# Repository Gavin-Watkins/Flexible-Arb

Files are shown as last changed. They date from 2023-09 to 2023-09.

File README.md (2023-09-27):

# Flexible Arduino Due based Arbitrary Signal Generator
Often during a project I have needed a complex test signal that is beyond the capability of the signal or function generators available in my lab. Commercial arbitrary signal generators (ARB) consisting of a fast memory coupled to a digital-to-analogue converter (DAC) are available, but often do not offer the right mix of analog and digital outputs in a suitably flexible (and affordable!) form. This has also been a problem during my day job where I have need to drive a high efficiency radio frequency (RF) power amplifiers (PA) or transmitters with two analogue outputs for the in-phase (I) and quadrature (Q) inputs of an RF modulator and several digital outputs for switching parts of the transmitter. [Previous work used an ARB platform developed around an Arduino Mega2560](https://www.researchgate.net/publication/361063526_A_Digital_Power_Amplifier_for_32-QAM). This was limited to a sample rate of 457kS/s. To increase the sample rate a new ARB has been developed based on an Arduino Due offering up to 8.4MS/s.

The Arduino Due is based on the 32-bit ATSAM3X8E allowing multiple 8-bit DACs and digital outputs to be mapped onto a single port. This ensuring all DAC or digital outputs update at the same time and only a single LUT is call for every update. The Arduino Due also runs at a higher clock rate of 84 MHz. Although 32-bit, none of the four ports (A to D) available on the ATSAM3X8E’s pins map to all 32-bits. Of the four ports, C with 24-bits available is the most useful. These 24 bits in this project are connected to two 8-bit DACs and one 8-bit digital port. However, they could for example drive two 12-bit DACs or any such combination.

# Testing the Arduino Due
The first thing anyone looks at with an ARB is the sampling rate. In a software based ARB like this (as oppose to an FPGA implementation) the microprocessor much fetch the output samples from memory and present them to the port with the DAC. This takes ten instruction cycles resulting in 8.4 MS/s as shown below in the minimum viable code:

start:                                // start of loop  

count = count + 1;                    // increment counter, takes two instruction

count = count & 0x000000FF;           // mask to prevent overflow from end of LUT, takes one instruction

PIOC->PIO_ODSR = Portvalues[count];   // access the LUT and send it to PortC, takes two instructions

goto start;                           // and repeat, takes five instructions

The felixbility of this option opens up other possiblities, like adding a second port which reads from its own LUT. PortA offers 23 bits, which would give a total of 47bits of data. This would however slow down the sample rate to 5.25 MS/s and require external latches for synchronising the data. This ran fastest when in Setup. Putting it in Loop resulted in slowing down. Why this is so, I'm not sure, but it is something I intend to explore further.

# DACs
The most important part of any ARB are the DACs. For this I settle on the DAC0801. Although quite old, they are readily available and easy to interface. Their datasheet quotes a settling time of 100ns consisting of the DAC slewing time and that for any ringing at the output to settle. The slewing time is a factor of the DAC output current and its load impedance. This suggests a maximum sample rate of 10 MS/s, which fits well with the 8.4 MS/s of the Due. The DAC0801 has complementary current sink outputs (pins 2 and 4). The datasheet suggests op-amp active current to voltage (I/V) converters as an output stage. This was found to introduce excess ringing, so passive resistive I/V converters were used instead. With a 1kΩ resistive load (RL) the slew rate was 30V/μs equivalent to a rise and fall time of 42ns. 

The DAC (IC1 and IC3) and op-amp (IC2 and IC4) interface is shown in the Eagle schematic "Sch6.sch" and as a png "Sch6.png". The peak output current of the DAC0801 is set at 2.13mA by the 4k7 resistors on pins 14 and 15 (R10, R14, R19 and R20) when a ±10V power supply is used. A 1k1 resistor tied to 0V and two 4k7 resistors in series (9k4) to +10 V positive supply rail add an offset so the output voltage at pin 4 swings positive and negative around 0V. This is a high impedance port so an op-amp with a gain of 2V/V buffers the output to drive 2V peak-to-peak into a 50Ω load. In the prototype a TL071 proved optimal in terms of bandwidth and ringing. Note in the schematic this is listed as a 741, simply because it was the first op-amp listed. The TL071 has a unity gain bandwidth product of 3MHz, reduced to 1.5MHz with a gain of 2V/V. Other op-amps may provide a better combination of bandwidth, slew rate and output current.

# Code
The Arduino Due can be programmed in the usual Arduino IDE, but has a unique set of instructions which allows direct port access. The following commands setup port C of the Due for direct access: PIOC→PIO_PER and PIOC→PIO_OER. The command PIOC→PIO_ODSR is then used to write data to the port. A goto loop sends data from the LUT to Port C runs in the setup, as using the main Void loop incurs various overheads including the I/O system to check the serial port. The result is 10 instructions and 8.4MS/s output rate. The LUT allocations are accessed by the variable count which is a 32-bit integer. This is masked (by ANDing) with FF (256) in the sinewave example, 1FF (512) in the triple test example and 4FFF (16384) for the 4G Long Term Evolution (LTE) signal example. Restricting the LUT to powers of 2 simplifies (and hence speeds up) the code. For other values an IF or FOR loop could be used to reset count at any value. A noInterrupts command to disable interrupts is included as without it jitter was noted on the output waveform suggesting the compiler sets some interrupts by default. If a lower sample frequency is desired though, the delayMicroseconds command can be included. In this case noInterrupts should be commented out.

# Data Generation
The data for all ports and the trigger signal are stored in a single LUT (Portvalues in the code). For Port C, the bits that are available on the external pins are: bits 1-8 for Ch A DAC, bits 12-19 for Ch B DAC, bits 21-26 for a digital interface and bit 28 as a trigger. These are generated individually and then mapped into a 32bit word which forms the values of Portvalues by multiplying the individual values by an offset and adding them together, for example:

Portvalues[X] = 2^28 x Trigger + 2^21 x Digital + 2^12 x DAC2 + 2 x DAC1

# Tool Chain 
The first two examples were generated in an OpenOffice spreadsheet (File "Signal Gen3.ods) as the LUTs were not very big. The third example was in Python ( due to the resulting LUT size. If using a spreadsheet the data will be generated in a single column. This can be copy and pasted directly into the Arduino IDE as a single column array. It is often more practical though to do this as a 2D array. The values from different cells can be combined with commas as a string into a single cell using the “&” function. In the sinewave example where the values of column Y are to be reformatted into a 16 column by 16 row for 256 values the following is used:

=Y2 & " , " & Y3 & ", " & Y4 & ", " & Y5 & ", " & Y6 & ", " & Y7 & ", " & Y8 & ", " & Y9 & ", " & Y10 & ", " & Y11 & ", " & Y12 & ", " & Y13 & ", " & Y14 & ", " & Y15 & ", " & Y16 & ", " & Y17 & ", "

Using the autofill function will not appropriately increment the Y column values, so there is still quite a bit of manual processing to be done, which is why for larger arrays it is appropriate to use Python. The Python code reads in the File "1M4LTE.txt". The sample rate of the LTE data is 7.68 MS/s, this is the original 122.88 MS/s downsampled by 16. Adding a dummy instruction to the Arduino code results in a sample rate of 7.64 MS/s. This is not close enough to 7.68 MS/s for standard compliance, but sufficient for measuring the adjacent channel power ratio (ACPR) of a PA/transmitter output.

# Hardware Implementation
To verify the concept, an Arduino Due “shield” was produced. This was fabricated on standard FR4 substrate using through hole DIL components. The layout is shown in "Sch6.brd" for Eagle and "Sch6_PCB.png" as a png. The Gerber files are in the zip file "Gerbers.zip". DIL components incur stray inductance and capacitance when operating in the MHz region, but allow the design to be easily modified. A surface mount implementation would probably produce better results than those presented here. 

The shield runs off a 5V supply for the digital and +/-10V for the analogue. The former can be extracted from the USB interface, as it is assumed that this project will be permanently connected to a computer for updating the LUT. The +/-10V can be derived from the 5V USB with a DC-DC converter and then smoothing and filtering.

# Example Results
The code includes three examples: a 32.8125kHz quadrature sinewave on DAC1 and DAC2 with a 256 value LUT (8.4MS/s / 256 = 32.8125 kHz), a triple tone test at around 1 MHz and the 4G LTE signal generation. Screen captures of these are shown to demonstrate the capabilities of the ARB. For the triple tone test the three tone frequencies are 984.375 kHz, 1.00078125 MHz and 1.0171875 MHz. These three resulting frequencies (Fr) were calculated with:

Fr = Fs * n / LUTs

Where Fs is the sampling frequency, n a whole number to avoid discontinuities – reducing spurious produces – and LUTs the LUT size. For an Fs was 8.4MS/s, n: 60, 61 and 62, and LUTs 512. Even with all the harmonically related spurious products, they are -38dB relative to the three tones. A higher resolution DAC would offer greater dynamic range, and hence lower spurious products. 

For the LTE signal, a screen capture of the spectrum of the I-channel signal is included. This includes guard channels, resulting in an actual RF bandwidth is 1.08MHz (consisting of six 180kHz resource blocks). The baseband bandwidth is half this, a spectrum of 504kHz as clearly shown in the example. The spectral regrowth is partially due to DAC non-linearities and also spurious products introduced by the system. uffers. The next phase of this research is to combine the LTE signal generator with a low-cost quadrature modulator development board to generate 4G signals for testing transmitter architectures.

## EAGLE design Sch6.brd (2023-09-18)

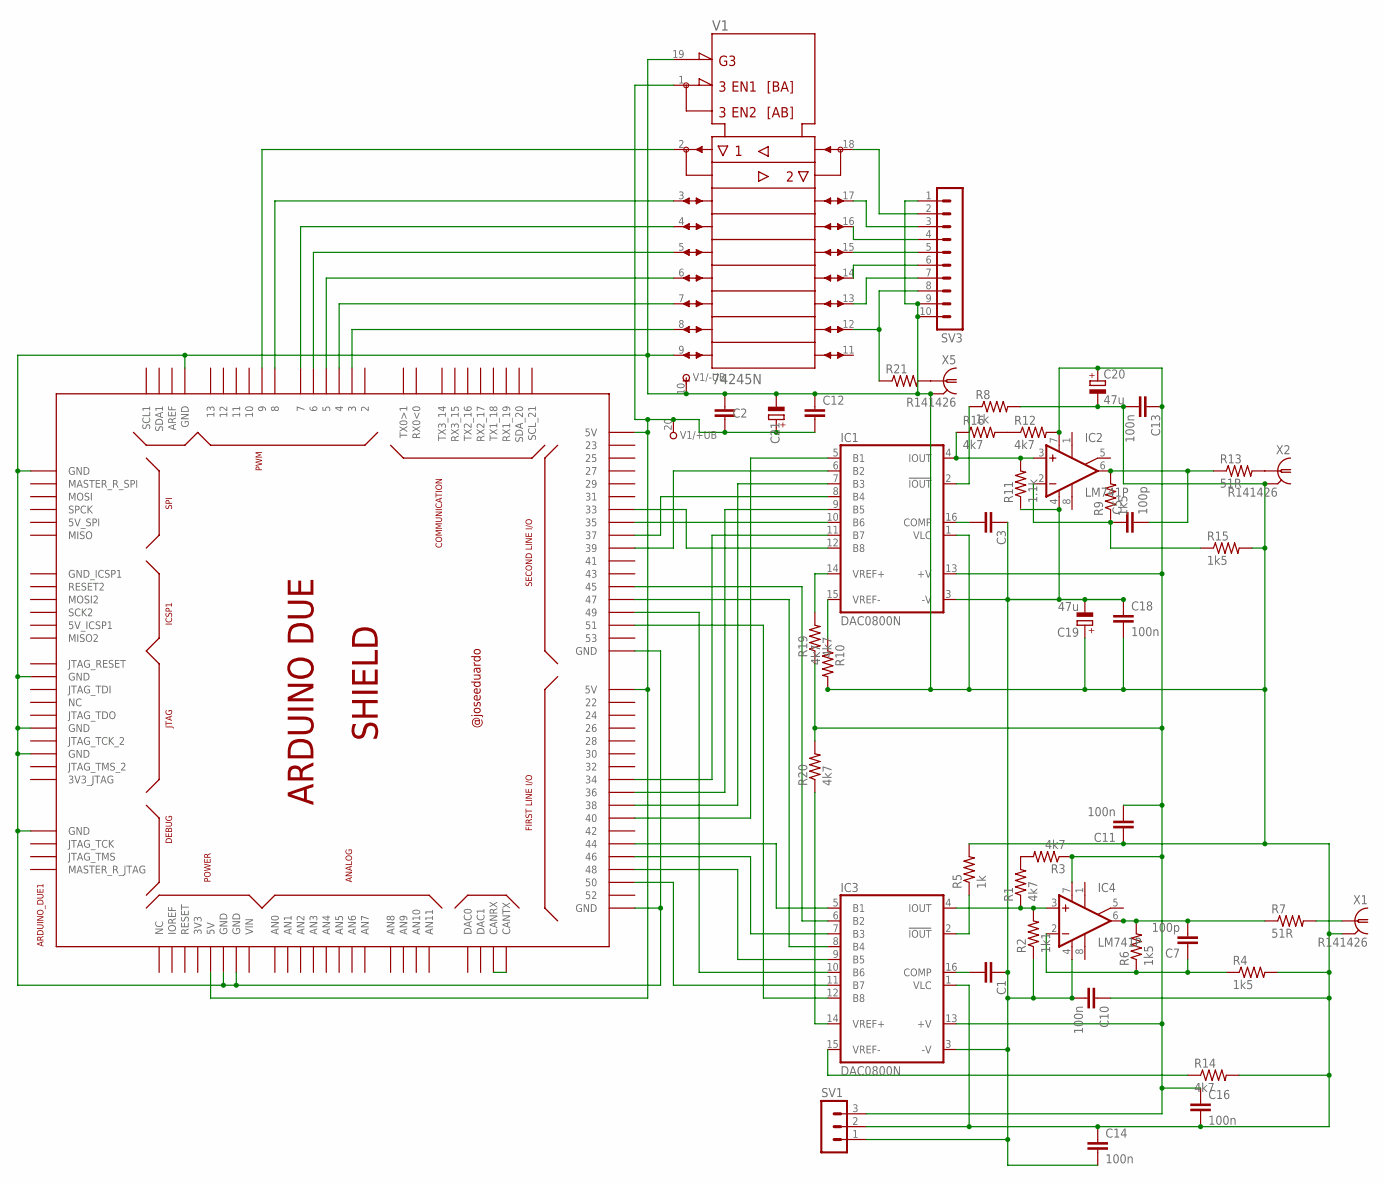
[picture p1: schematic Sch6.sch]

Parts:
ARDUINO_DUE1: ARDUINO_DUE_SHIELD
C1, C2, C3, C12: C-EU050-025X075; C050-025X075
C5, C7: 100p; C050-025X075
C10, C11, C13, C14, C16, C18: 100n; C050-025X075
C19, C20: 47u; E5-10,5
C21: CPOL-EUE5-10.5; E5-10,5
IC1, IC3: DAC0800N; DIL16
IC2, IC4: LM741P; DIL08
R1, R3, R10, R12, R14, R16, R19, R20: 4k7; 0207/10
R2: 1k1; 0207/10
R4, R6, R9, R15: 1k5; 0207/10
R5, R8: 1k; 0207/10
R7, R13: 51R; 0207/10
R11: 1.1k; 0207/10
R21: R-US_0207/10; 0207/10
SV1: MA03-1
SV3: MA10-1
V1: 74245N; DIL20
X1, X2, X5: R141426

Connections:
unnamed: ARDUINO_DUE1.51, IC3.12 (B8)
unnamed: R21.2, X5.1
unnamed: ARDUINO_DUE1.33, IC1.12 (B8)
unnamed: IC1.2 (!IOUT), R8.1
unnamed: ARDUINO_DUE1.9, V1.2 (A1)
unnamed: ARDUINO_DUE1.34, IC1.11 (B7)
unnamed: ARDUINO_DUE1.50, IC3.11 (B7)
unnamed: ARDUINO_DUE1.35, IC1.10 (B6)
unnamed: ARDUINO_DUE1.36, IC1.9 (B5)
unnamed: ARDUINO_DUE1.37, IC1.8 (B4)
unnamed: ARDUINO_DUE1.49, IC3.10 (B6)
unnamed: ARDUINO_DUE1.CANRX, ARDUINO_DUE1.CANTX
unnamed: ARDUINO_DUE1.5V0 (5V), ARDUINO_DUE1.5V0_1 (5V), ARDUINO_DUE1.5V0_2 (5V), C2.2, C12.2, C21.+, V1.1 (DIR), V1.20 (+UB)
unnamed: ARDUINO_DUE1.38, IC1.7 (B3)
unnamed: ARDUINO_DUE1.39, IC1.6 (B2)
unnamed: ARDUINO_DUE1.8, V1.3 (A2)
unnamed: ARDUINO_DUE1.40, IC1.5 (B1)
unnamed: ARDUINO_DUE1.48, IC3.9 (B5)
unnamed: ARDUINO_DUE1.47, IC3.8 (B4)
unnamed: R1.2, R3.2
unnamed: ARDUINO_DUE1.45, IC3.6 (B2)
unnamed: IC3.4 (IOUT), IC4.3 (+IN), R1.1, R2.2
unnamed: ARDUINO_DUE1.7, V1.4 (A3)
unnamed: ARDUINO_DUE1.6, V1.5 (A4)
unnamed: ARDUINO_DUE1.5, V1.6 (A5)
unnamed: ARDUINO_DUE1.4, V1.7 (A6)
unnamed: ARDUINO_DUE1.3, V1.8 (A7)
unnamed: SV3.5, V1.15 (B4)
unnamed: SV3.6, V1.14 (B5)
unnamed: SV3.7, V1.13 (B6)
unnamed: R21.1, SV3.8, V1.12 (B7)
unnamed: SV3.4, V1.16 (B3)
unnamed: SV3.3, V1.17 (B2)
unnamed: SV3.2, V1.18 (B1)
unnamed: C11.2, C13.1, C16.1, C20.+, IC1.13 (+V), IC2.7 (V+), IC3.13 (+V), IC4.7 (V+), R3.1, R12.2, R19.1, R20.2, SV1.3
unnamed: ARDUINO_DUE1.GND, ARDUINO_DUE1.GND_1 (GND), ARDUINO_DUE1.GND_2 (GND), ARDUINO_DUE1.GND_3 (GND), ARDUINO_DUE1.GND_4 (GND), ARDUINO_DUE1.GND_5 (GND), ARDUINO_DUE1.GND_7 (GND), ARDUINO_DUE1.GND_8 (GND), ARDUINO_DUE1.GND_9 (GND), ARDUINO_DUE1.GND_10 (GND), C2.1, C10.1, C11.1, C12.1, C13.2, C14.1, C16.2, C18.2, C19.+, C20.-, C21.-, IC1.1 (VLC), IC3.1 (VLC), R4.2, R5.2, R8.2, R10.2, R14.2, R15.2, SV1.2, SV3.1, SV3.9, SV3.10, V1.9 (A8), V1.10 (-UB), V1.19 (!G), X1.2, X1.3 (2), X1.4 (2), X1.5 (2), X2.2, X2.3 (2), X2.4 (2), X2.5 (2), X5.2, X5.3 (2), X5.4 (2), X5.5 (2)
unnamed: R12.1, R16.2
unnamed: ARDUINO_DUE1.46, IC3.7 (B3)
unnamed: C3.2, IC1.16 (COMP)
unnamed: ARDUINO_DUE1.44, IC3.5 (B1)
unnamed: C1.2, IC3.16 (COMP)
unnamed: C5.1, IC2.2 (-IN), R9.1, R15.1
unnamed: IC1.4 (IOUT), IC2.3 (+IN), R11.2, R16.1
unnamed: C7.1, IC4.2 (-IN), R4.1, R6.1
unnamed: IC3.2 (!IOUT), R5.1
unnamed: C1.1, C3.1, C10.2, C14.2, C18.1, C19.-, IC1.3 (-V), IC2.4 (V-), IC3.3 (-V), IC4.4 (V-), R2.1, R11.1, SV1.1
unnamed: C7.2, IC4.6 (OUT), R6.2, R7.1
unnamed: R7.2, X1.1
unnamed: C5.2, IC2.6 (OUT), R9.2, R13.1
unnamed: R13.2, X2.1
unnamed: IC1.15 (VREF-), R10.1
unnamed: IC3.15 (VREF-), R14.1
unnamed: IC1.14 (VREF+), R19.2
unnamed: IC3.14 (VREF+), R20.1

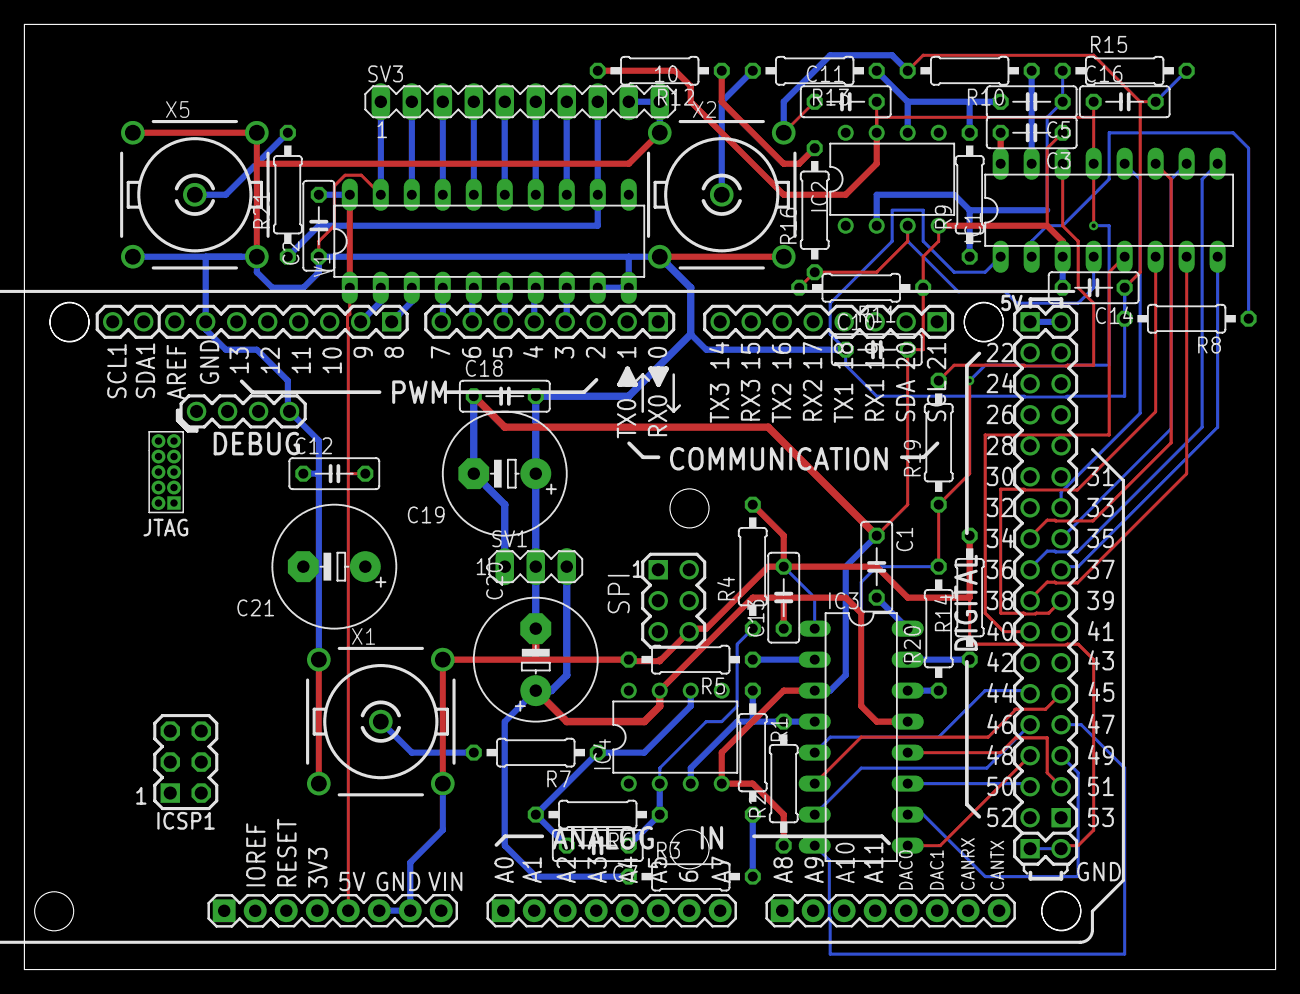
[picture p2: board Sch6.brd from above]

Board: 2 copper layers, 102.5 x 77.5 mm, 45 parts (0 on the bottom side), 54 nets.
